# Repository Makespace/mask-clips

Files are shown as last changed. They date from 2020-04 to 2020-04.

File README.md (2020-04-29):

# Makespace Mask Clips

The documents covering the regulation, design and production of the Makespace Mask Clips

For the high-level overview of this activity, see https://web.makespace.org/covid-19/mask-clips/

* _Requirements_ – The device specification, regulations and risk assessments
* _Design Files_ – The mask clip design files
* _Materials_ – The materials and data sheets
* _Production_ – Manufacturing Standard Operating Procedure (SOP), Training and Worker/Batch Tracking
* _Documentation_ – The accompanying documentation and labelling for shipping

The _Manufacturing SOP_ document found in the _production_ directory is the key document describing the whole process, and the place to start if you want to learn about the activity.

The _Workstation Single Point Lessons_ ppt is also useful to get a feel for the activities that need to be performed.

The _requirements_ directory is good reading for context on how the essential safety requirements mandated in regulations are fulfilled by the design and documentation. This is what is required when the UK government relaxed the rules on PPE for hospitals from ‘at least CE marked’ to ‘meet essential safety requirements’.

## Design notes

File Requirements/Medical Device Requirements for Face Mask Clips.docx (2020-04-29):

Surgical Face Masks - For Clips Project

Surgical masks are Class 1 Medical Device.

“masks for the protection of the user (e.g. from the environment) are not medical devices, however, surgical masks (for use in an operating theatre) are medical devices as they are intended to protect the patient rather than the user”

Reference: https://assets.publishing.service.gov.uk/government/uploads/system/uploads/attachment_data/file/284505/Borderlines_with_medical_devices.pdf

Standard for surgical masks: Medical Face Masks - BS EN 14683:2019

“The main intended use of medical face masks is to protect the patient from infective agents and, additionally, in certain circumstances to protect the wearer against splashes of potentially contaminated liquids. Medical face masks may also be intended to be worn by patients and other persons to reduce the risk of spread of infections, particularly in epidemic or pandemic situations.”

“Type I medical face masks are used for patients in order to reduce the risk of the spread of infections, particularly in epidemic or pandemic situations. Type II masks are principally intended for use by healthcare professionals in an operating room or other medical settings with similar requirements.”

“The level of efficiency offered by a mask depends on a number of factors such as the filtration efficiency, quality of the material and the fit of the mask on the wearer’s face. Different designs are suited for different applications and the careful choice of mask is therefore important in order to achieve the desired result.”

“Due to the fact that used masks are considered highly contaminated, it is essential that:

— | the body of the mask is not touched by the fingers/hands of the wearer;”
— | a mask is worn covering the nose and mouth of the wearer, at no time a mask is hanging around the neck of the wearer”

- Use of the clip must not reduce Particle filtration, Bacterial Filtration, Breathability or blood fluid penetration

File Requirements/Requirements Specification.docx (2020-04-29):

# Requirements Specification

# 1. General Device Description & Intended Purpose

The product is a disposable cardboard attachment which sits on the back of the user’s head and is used to secure the elastic ear loops of disposable surgical masks.

It is intended to be used:

- To improve security of disposable Type IIR surgical masks with elastic ear loops against face compared to having no extra securement method
- To be more comfortable than the current recommended securement method (knots tied in the ear loops)

Type IIR surgical masks are a Class 1 medical device, and as such the face mask clip is an accessory to a medical device.

# 2. Specifications for Product

## 2.1. User Requirements

- The clip should deliver increased ear comfort compared to current best practice for surgical masks with ear loops (knotted ear loops)
- The clip should enable surgical masks with ear loops to be tightened such that they fit closely to the face
- Clip should be manufacturable at scale: projected best case 88635 surgical masks used in April (worst case: 354540)
- The clip is single use so disposable alongside face mask
- Clip must allow for different head sizes and be adjustable for tightness and comfort
- The edges and corners should not be sharp, such that they could rip gloves or cause injury
- Robust in expected usage conditions
- The clip must be suitable for a patient to wear whilst lying in bed
- There should be no increased risk of COVID infection due to use of the clip compared to current best practice
  2.2. Specification

User Requirement | Specification
The clip should deliver increased ear comfort compared to current best practice for surgical masks with ear loops (knotted ear loops) | Design must prevent the elastic ear loops being tightened against the user’s ears
The clip should enable surgical masks with ear loops to be tightened such that they fit closely to the face | The clip should enable surgical masks with ear loops to be tightened such that they fit closely to the face, such that the fit is as effective (or better) as with knotted ear loops
Clip should be manufacturable at scale: projected best case 88635 surgical masks used in April (worst case: 354540) | Design suitable for mass production of at least 10,000 units per day
The clip is single use so disposable alongside face mask | < 10p per item
| Suitable for incineration
| Minimum material per clip
Clip must allow for different head sizes and be adjustable for tightness and comfort | Design should enable users to adjust tightness
The edges and corners should not be sharp, such that they could rip gloves or cause injury | No sharp corners/edges
Robust in expected usage conditions | The clip must not break for a maximum usage duration of 4 hrs
The clip must be suitable for a patient to wear whilst lying in bed | Clip profile flat against head, no protrusions
There should be no increased risk of COVID infection due to use of the clip compared to current best practice | Must be provided clean (but not sterile, does NOT need to be sterilisable or resistant to cleaning products)
| Should not incur increased handling of ‘dirty’ PPE or hair/face/head when doffing
| The clip should not impact the usage or security of other PPE

Monitoring compliance with and the effectiveness of this document

This process forms part of a quality system accredited to International Standard EN ISO 9001:2015, EN ISO 13485:2016 and BS 70000:2017. The effectiveness of the process will be monitored in accordance with the methods given in the Quality Manual (CE-QS-QAM-4).

Equality and diversity statement

This document complies with the Cambridge University Hospitals NHS Foundation Trust service equality and diversity statement.

Disclaimer

It is your responsibility to check against the electronic library that this printed out copy is the most recent issue of this document.

Document management

Approval: | Sarah Greasley
MDAG approval:
Owning department: | Clinical Engineering Innovation
Author(s): | Sonya Sireau
Pharmacist: | n/a
File name: | Device Verification and Validation
Supersedes: | n/a
Version number: | 1.0 | Review date: | n/a
Local reference: | | Document ID:

Cambridge University Hospitals NHS Foundation Trust Requirements Specification

Clinical Engineering Innovation Medical Physics and Clinical Engineering

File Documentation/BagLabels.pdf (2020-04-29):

### Mask Clip

Design:
Lot No:
Name of Cutter:
Name of QC:
Date:
Material Batch No:
Number of Sheets:

### Mask Clip

Design:
Lot No:
Name of Cutter:
Name of QC:
Date:
Material Batch No:
Number of Sheets:

### Mask Clip

Design:
Lot No:
Name of Cutter:
Name of QC:
Date:
Material Batch No:
Number of Sheets:

### Mask Clip

Design:
Lot No:
Name of Cutter:
Name of QC:
Date:
Material Batch No:
Number of Sheets:

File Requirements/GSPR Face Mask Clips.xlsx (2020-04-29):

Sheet: Guidance
Template Q-pulse Reference: CE-ER-FRM-25 Revision 5
How to Complete the Checklist
Identity of the device | The manufacturer should identify the device, and where applicable the various configurations / variants covered by the checklist.
A. General Safety and Performance Requirements | Description of the Safety and Performance Requirements (SPR) as found in Annex I of the Medical Devices Regulation. The text is included non-edited. Also referred to as Essential Principle (EP)
B. Applicable to the device? | Is the listed Essential Principle applicable to the device? Here the answer is either ‘YES’ or ‘NO’. If the answer is ‘NO’ this should be explained briefly in the ‘method used to demonstrate conformity’ column. Example: For a device that does not incorporate biological substances, the answer to Essential Principle 5.8.2 would be ‘NO’ and, in the ‘method used to demonstrate conformity’ column, would include an explanation such as ‘The device does not incorporate biological substances.’
A / NA: | Identification whether the specific SPR is applicable (A) or not applicable (NA).
NOTE: It is required by the regulation to explain the reason why an essential requirement is not applicable. (e.g. for SPR 21 that the device is not connected to or equipped with a power source)
C. Method used to demonstrate conformity | In this column the manufacturer should state the type(s) of method(s) that they have chosen to use to demonstrate conformity e.g. the recognised standard(s), industry or in-house test method(s), comparison study(ies) or other method used.
D-F. Method reference | After having stated the method in the previous column, here the manufacturer should now name the title and reference of the recognised standard(s), industry or in-house test method(s), comparison study(ies) or other method used to demonstrate conformity. For standards, this should include the date of the standard and where appropriate, the clause(s) that demonstrates conformity with the relevant EP.
Horizontal Standards: | Specifies the relevant horizontal standards (horizontal standards are standards applicable to a broad range of medical devices, e.g. to electrically operated medical devices in general – e.g. EN 60601-1). Include the date of the standard and where appropriate, the clause(s) that demonstrates conformity with the relevant EP.
Vertical Standards: | Specifies the relevant vertical standards (vertical standards are standards applicable to a much more narrow range of products, e.g. to electrically operated infusions pumps – e.g. EN 60601-2-24). Include the date of the standard and where appropriate, the clause(s) that demonstrates conformity with the relevant EP.
Other Compliance Documentation: | Where a standard is not the appropriate means of ensuring compliance, identifies the method for alternative compliance documentation (e.g. in-house test method, etc.).
NOTE. When a requirement is dealt with in a horizontal as well as in a vertical standard, preference should be given to the more product specific standard, i.e. to the vertical standard
G. Reference to supporting controlled documents | This column should contain the reference to the actual technical documentation that demonstrates conformity to the essential principle, i.e. the certificates, test reports, validation reports, study reports or other documents that resulted from the method used to demonstrate conformity and its location within the STED.
Technical File Reference: | Reference to the Technical File information - Title and Q-pulse reference
NOTE: Machinery Directive | For medical devices which are also machinery within the meaning of Article 2 (a) of Directive 2006/42/EC on machinery:
 | Where relevant hazard exists, devices shall also meet the essential health and safety requirements of the Machinery Directive to the extent to which those essential health and safety requirements are MORE SPECIFIC than the essential requirements of the MDD (93/42/EEC)
Guidance from Global Harmonization Task Force GHTF/SG1/NO11:2008 (STED)
http://www.imdrf.org/docs/ghtf/archived/SG1/technical-docs/ghtf-sg1-n011-2008-principles-safety-performance-medical-devices-080221.pdf

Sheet: SPR Safety & Performance
Document Q-pulse reference:
Product identification (Identity of the Device): | Face Mask Clips
Author: | Sarah Greasley
Date: | 22/04/20
GENERAL SAFETY AND PERFORMANCE REQUIREMENTS CHECKLIST | Applicable to the device? | Method used to demonstrate conformity | Method reference |  |  | Reference to supporting controlled documents
GENERAL SAFETY AND PERFORMANCE REQUIREMENTS | A/NA | Method | Horizontal Standards | Vertical Standards | Other Compliance Documentation | Technical File Reference
1. Devices shall achieve the performance intended by their manufacturer and shall be designed and manufactured in such a way that, during normal conditions of use, they are suitable for their intended purpose. They shall be safe and effective and shall not compromise the clinical condition or the safety of patients, or the safety and health of users or, where applicable, other persons, provided that any risks which may be associated with their use constitute acceptable risks when weighed against the benefits to the patient and are compatible with a high level of protection of health and safety, taking into account the generally acknowledged state of the art. | A | Statement of Intended purpose Risk File
2. The requirement in this Annex to reduce risks as far as possible means the reduction of risks as far as possible without adversely affecting the benefit-risk ratio. | A | Risk File
3. Manufacturers shall establish, implement, document and maintain a risk management system. | A | Risk Management Process
Risk management shall be understood as a continuous iterative process throughout the entire lifecycle of a device, requiring regular systematic updating. In carrying out risk management manufacturers shall: | A | Risk Management Process
(a) establish and document a risk management plan for each device; | A | Risk Plan
(b) identify and analyse the known and foreseeable hazards associated with each device; | A | Risk File
(c) estimate and evaluate the risks associated with, and occurring during, the intended use and during reasonably foreseeable misuse; | A | Risk File
(d) eliminate or control the risks referred to in point (c) in accordance with the requirements of Section 4; | A | Risk File
(e) evaluate the impact of information from the production phase and, in particular, from the post-market surveillance system, on hazards and the frequency of occurrence thereof, on estimates of their associated risks, as well as on the overall risk, benefit-risk ratio and risk acceptability; and | A | Risk File PMS will also be conducted by speaking to the infection control team and asking for feedback from clinicians using the devices
(f) based on the evaluation of the impact of the information referred to in point (e), if necessary amend control measures in line with the requirements of Section 4. | A | Risk File
4. Risk control measures adopted by manufacturers for the design and manufacture of the devices shall conform to safety principles, taking account of the generally acknowledged state of the art. To reduce risks, Manufacturers shall manage risks so that the residual risk associated with each hazard as well as the overall residual risk is judged acceptable. In selecting the most appropriate solutions, manufacturers shall, in the following order of priority: | A | Risk File IFU / Training Manufacturing Documentation
(a) eliminate or reduce risks as far as possible through safe design and manufacture;
(b) where appropriate, take adequate protection measures, including alarms if necessary, in relation to risks that cannot be eliminated; and
(c) provide information for safety (warnings/precautions/contra-indications) and, where appropriate, training to users.
Manufacturers shall inform users of any residual risks. | A | IFU
5. In eliminating or reducing risks related to use error, the manufacturer shall: | N/A | N/A
(a) reduce as far as possible the risks related to the ergonomic features of the device and the environment in which the device is intended to be used (design for patient safety), and | A | The device will be shown to a clinican for feedback on the ergonomics of the design. This information will feed in to the risk file
(b) give consideration to the technical knowledge, experience, education, training and use environment, where applicable, and the medical and physical conditions of intended users (design for lay, professional, disabled or other users). | A | Feedback from the intended users will be obtained and incorpoorated into the design / IFU
6. The characteristics and performance of a device shall not be adversely affected to such a degree that the health or safety of the patient or the user and, where applicable, of other persons are compromised during the lifetime of the device, as indicated by the manufacturer, when the device is subjected to the stresses which can occur during normal conditions of use and has been properly maintained in accordance with the manufacturer's instructions. | A | The devices will be clearly labelled as single use. They will be designed and tested to be durable for this duration
7. Devices shall be designed, manufactured and packaged in such a way that their characteristics and performance during their intended use are not adversely affected during transport and storage, for example, through fluctuations of temperature and humidity, taking account of the instructions and information provided by the manufacturer. | A | Design and Manufacture Documentation No materials used will be affected by conditions likley to be experienced during distribution or storage
8. All known and foreseeable risks, and any undesirable side-effects, shall be minimised and be acceptable when weighed against the evaluated benefits to the patient and/or user arising from the achieved performance of the device during normal conditions of use. | A | Risk File
9. For the devices referred to in Annex XVI, the general safety requirements set out in Sections 1 and 8 shall be understood to mean that the device, when used under the conditions and for the purposes intended, does not present a risk at all or presents a risk that is no more than the maximum acceptable risk related to the product's use which is consistent with a high level of protection for the safety and health of persons. | A | Statement of Intended purpose Risk File
REQUIREMENTS REGARDING DESIGN AND MANUFACTURE
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

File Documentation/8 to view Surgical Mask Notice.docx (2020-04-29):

Disposable Surgical Mask Clips 002 DIRECTIONS FOR USE: This product is designed and intended only as a method of securing the elastic ear loops on surgical masks. This is a single use product. Dispose of product after use. One Size fits all. NON-STERILE. THIS PRODUCT IS NOT CE-MARKED. IT IS ONLY FOR USE DURING THE COVID-19 OUTBREAK Class I medical device Clinical Engineering, Box 152, Addenbrooke's Hospital, Cambridge, CB2 0QQ | Disposable Surgical Mask Clips 002 DIRECTIONS FOR USE: This product is designed and intended only as a method of securing the elastic ear loops on surgical masks. This is a single use product. Dispose of product after use. One Size fits all. NON-STERILE. THIS PRODUCT IS NOT CE-MARKED. IT IS ONLY FOR USE DURING THE COVID-19 OUTBREAK Class I medical device Clinical Engineering, Box 152, Addenbrooke's Hospital, Cambridge, CB2 0QQ
Disposable Surgical Mask Clips 002 DIRECTIONS FOR USE: This product is designed and intended only as a method of securing the elastic ear loops on surgical masks. This is a single use product. Dispose of product after use. One Size fits all. NON-STERILE. THIS PRODUCT IS NOT CE-MARKED. IT IS ONLY FOR USE DURING THE COVID-19 OUTBREAK Class I medical device Clinical Engineering, Box 152, Addenbrooke's Hospital, Cambridge, CB2 0QQ | Disposable Surgical Mask Clips 002 DIRECTIONS FOR USE: This product is designed and intended only as a method of securing the elastic ear loops on surgical masks. This is a single use product. Dispose of product after use. One Size fits all. NON-STERILE. THIS PRODUCT IS NOT CE-MARKED. IT IS ONLY FOR USE DURING THE COVID-19 OUTBREAK Class I medical device Clinical Engineering, Box 152, Addenbrooke's Hospital, Cambridge, CB2 0QQ
Disposable Surgical Mask Clips 002 DIRECTIONS FOR USE: This product is designed and intended only as a method of securing the elastic ear loops on surgical masks. This is a single use product. Dispose of product after use. One Size fits all. NON-STERILE. THIS PRODUCT IS NOT CE-MARKED. IT IS ONLY FOR USE DURING THE COVID-19 OUTBREAK Class I medical device Clinical Engineering, Box 152, Addenbrooke's Hospital, Cambridge, CB2 0QQ | Disposable Surgical Mask Clips 002 DIRECTIONS FOR USE: This product is designed and intended only as a method of securing the elastic ear loops on surgical masks. This is a single use product. Dispose of product after use. One Size fits all. NON-STERILE. THIS PRODUCT IS NOT CE-MARKED. IT IS ONLY FOR USE DURING THE COVID-19 OUTBREAK Class I medical device Clinical Engineering, Box 152, Addenbrooke's Hospital, Cambridge, CB2 0QQ
Disposable Surgical Mask Clips 002 DIRECTIONS FOR USE: This product is designed and intended only as a method of securing the elastic ear loops on surgical masks. This is a single use product. Dispose of product after use. One Size fits all. NON-STERILE. THIS PRODUCT IS NOT CE-MARKED. IT IS ONLY FOR USE DURING THE COVID-19 OUTBREAK Class I medical device Clinical Engineering, Box 152, Addenbrooke's Hospital, Cambridge, CB2 0QQ | Disposable Surgical Mask Clips 002 DIRECTIONS FOR USE: This product is designed and intended only as a method of securing the elastic ear loops on surgical masks. This is a single use product. Dispose of product after use. One Size fits all. NON-STERILE. THIS PRODUCT IS NOT CE-MARKED. IT IS ONLY FOR USE DURING THE COVID-19 OUTBREAK Class I medical device Clinical Engineering, Box 152, Addenbrooke's Hospital, Cambridge, CB2 0QQ | Basmati Rice 2015-01-22

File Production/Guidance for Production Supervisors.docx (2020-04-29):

# Makespace Surgical Mask Clip Production: Guidance for Production Supervisors

# Who Can Be a Production Supervisor?

The production supervisor should:

- Be familiar with every process involved in manufacturing, i.e. have been a volunteer on at least one previous shift
- Be a current Makespace member.
- Be trained on the laser-cutter, or have someone present who is.

# Planning

First-time supervisors should be supported by someone who has supervised a shift, or is familiar with most of the processes, e.g. Alaric or Jonathan. It may not be necessary for that person to be there for the whole time, but make sure you know who will be supporting you, and have contact numbers for arising issues.

Many people have worked extremely hard to set up production of the clips. You will be aware that part of the reason you are supervising a shift is so that they can have a rest. You should therefore be aware of common issues which are likely to arise, so you can handle them without contacting people outside the space. Equally, we have an obligation to manufacture to an acceptable standard, and if you’re not confident that can be achieved, it is better to call someone and get help than risk producing an unacceptable product.

## Issues that May Arise

The following things are the most likely, and you should know what to do or who to contact if they happen:

- Fire in the laser cutter, and or setting off the fire alarm
  - As per standard laser cutter practice, If the fire can be safely dealt with, blow it out (remember to remove mask), or use the fire extinguisher under the desk between the laser cutters. Otherwise raise the alarm with the break glass next to the exit door. The fire assembly point is in the main carpark out the front.
  - If the fire alarm goes off but the fire has been extinguished, call the estates department and let them know, so that the fire crew isn’t called out.
- Needing something from the office (e.g. packing tape, nitrile gloves). Will there be someone on shift with access (directors, some equipment owners)?
- Questions about the process, e.g. what quality issues are acceptable. You should be familiar with most of the things that can go wrong, e.g.smoke stains, burn marks Familiarise yourself with the operating procedures (SOP). (https://drive.google.com/open?id=1OLOXmGqOo-xyjaSSg0BIGB7wWn_eqW5IFoa0JmBFgyE) Try to answer most questions yourself, remember if it’s only one or two clips affected, it’s safer to reject them. Don’t worry about the occasional false-reject.
- Errors with data entry. Volunteers will sometimes make errors, e.g. forgetting to retire jobs, selecting the wrong job etc. If Dan is there, he can correct those. If you are confident to do so, you can correct them yourself in the production spreadsheet (https://drive.google.com/open?id=1U6qBrt-kxL_5vciE0YUX_pbPlAORHrKN3EtSc_qxcnQ).
- Process Changes. Volunteers may suggest process changes and improvements. If they can be included within the existing SOPs, they may be acceptable. If not, they should be rejected or approved by Mark Mellors.

# Running the Shift

1. Try to speak with the production supervisor for the previous shift before that shift ends, so you understand any issues such as shortages before your shift starts.
2. Arrive about 30-60 minutes before the shift starts to give time for reviewing the state of the workplace, cleaning, and any corrective actions needed. If you’re running an afternoon shift after a morning shift has run, you should be able to speak with the previous supervisor then.
3. When the volunteers arrive, brief them on:
  a. Building issues: Fire safety - fire extinguisher location, break glass, locations of exits; Toilets; Breakroom. Clean area and dirty area.
  b. Check if they are symptomatic or have been exposed. Send home if exposed in the last 14 days.
  c. Procedure for cleaning and doffing PPE. check no-one is wearing a valved mask - replace with a cotton one or cover the valve
  d. How to use the IT system, and why (medical manufacturing, traceability).
4. Anyone who arrives early can start on any outstanding cleaning.
5. Assign people to workstations, and ensure they are trained, either by another volunteer, or yourself. After a few minutes, check on them to make sure they’re happy with what they’re doing, and following procedures. Periodically check in with people, and check that they’re retiring cards correctly.
6. Try to keep work flowing consistently through the process. There should be roughly equal numbers of batches queued at each station. If one process is getting ahead or behind, move volunteers around to balance it out. This will help to minimise work in progress (WIP).
7. Encourage volunteers to work in full batches, and not stop mid-batch. Organising a tea-break in the middle of the shift is usually welcome!
8. Keep an eye on stock levels, both of WIP and input materials, to avoid bottlenecks.
9. At the end of the shift, all workstations should be tidied ready for the next shift. Ensure that there are no partially-completed batches. Warn volunteers before the end of the shift, so that they don’t start batches without time to complete them.
10. Ensure all the volunteers sign out when they leave.

# Production Database Cheat Sheet

The Chrome-books which are set up at each station for production tracking feed into this database: production spreadshee (https://drive.google.com/open?id=1L1GX-7yRM-hOOdorrYTUK3-CFr-ufjhGhRJ_fhcEF2Y)t, on the ‘JobLog’ tab. Further details about the spreadsheet will be documented in the README (https://github.com/axiomsofchoice/jobcardsystem) of the published source code

Key operations you should be aware of:

1. Comments can always be added in the comments column, separated by a ‘;’. E.g. if there is already a comment, add a ‘;’, then your comments.
2. If you make a change, add a comment, e.g. Fixed consumed job, used 101, not 100.
3. Sometimes volunteers put in the wrong ‘consumed lots’ information. If you know what they did, you can correct the lots consumed by changing the numbers in this column.
4. Periodically check the contents of each of the tabs in the spreadsheet in case there is an issue that needs to be brought to someone’s attention (e.g. someone ticks yes for has symptoms) or there is a data entry issue that needs correcting. Important: values in the comments column are not automatically used for traceability, they are only for humans, so ensure the values in the “Lots Consumed” column accurately reflect what occurred.
5. The values recorded in “Worker”, “Additional Worker 1”, “Additional Worker 2” and “Retired by” must correspond precisely to the values given in the “Workers” sheet, including case and spelling.
6. Often, volunteers forget to retire jobs after they have been consumed. You can retire a job by going to the home page and selecting “Retire Job Card”.
7. If a volunteer forgets to mark a job as complete there is currently no way to correct this in the UI and it must be corrected via the spreadsheet.
8. If a volunteer accidentally retires a job, you can ‘unretire’ it by clearing the “Lot Consumed Time” and “Retired by” entries for that job.
9. Duplicate jobs sometimes occur although now less frequently. If this happens, identify the job that should not be there and change the workstation to “Void”, appending a note in the comment field.
10. At the end of a shift, a backup should be made of the spreadsheet, which can be done by going to File > Download.
11. Any bugs can be raised on the Github issue tracker (https://github.com/axiomsofchoice/jobcardsystem/issues).

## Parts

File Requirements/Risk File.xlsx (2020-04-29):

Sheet: Title
Medical Physics and Clinical Engineering |  |  |  | Addenbrookes Hospital
Clinical Engineering / R&D
Risk File |  |  |  | CE-ER-FRM-22
 |  | Product Identification | Surgical Mask Clips
 |  | Document Q-Pulse reference
 |  | Doc. Name | Risk File - Mask Clips
 |  | Mandatory Supporting Documents | Q-Pulse reference
 |  | Risk Management Process
 |  | Risk Plan
 |  | Risk Report
 | Product description and intended use
 | The product is a disposable attachment which is used to secure the elastic ear loops of disposable surgical masks by providing an attachment point on the back of the head. It is intended to be used: To improve security of disposable Type IIR surgical masks with elastic ear loops against face compared to having no extra securement method To be more comfortable than the current recommended securement method (knots tied in the ear loops) Type IIR surgical masks are a Class 1 medical device, and as such the face mask clip is an accessory to a medical device.
Cambridge University Hospitals NHS Foundation Trust |  |  |  |  | Page 1 of 4
This document complies with the Cambridge University Hospitals NHS Foundation Trust service Equality and Diversity statement and must be read in conjunction with Addenbrookes Hospital Policies & Procedures. It is your responsibility to check against the electronic library that this printed out copy is the most recent issue of this document. All changes required should be submitted via Q-Pulse Document module (Change request).
Filename: 008_Risk Evaluation Table
Document No.: CE-ER-FRM-15 |  |  | Version No.: 5 | Active on Q-Pulse & Published

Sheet: Revision Table
Document History
Date | Identification | Description | Name
2020-08-04 | 1.0 | Created (Draft) | Sonya Sireau

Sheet: Risk Evaluation Criteria
CUH Risk management strategy and policy 2019-2019
 | CUH Risk management strategy and policy 2019-2020
Source | CUH Risk management strategy and policy 2019-2020, http://merlin/Lists/DMSRecords/DispRecordTabsDoc.aspx?ID=18427
Adaptations | The risk scoring matrix and grading system has been adapted to enable the CEI team to better track and manage risks that are yet to be determined, or cannot be determined.
Notes | Risk evaluation is for injury or damage to the health of people, or damage to property or the environment, and does include risks surrounding data security. It should NOT consider project or financial impacts. These should instead be considered in the Project Viability Assessment.
 | Risk Evaluation
 | Severity Score |  | Likelihood Score |  |  |  |  |  |  | Grading Risk
 |  |  | 1 | 2 | 3 | 4 | 5 | TBD | CBD | 1-3 | Low risk | No action required
 |  |  | Rare | Unlikely | Possible | Likely | Almost Certain | To be determined | Cannot be determined | 4-6 | Moderate risk | Risk reduction if practicable
 | 1 | Negligible | 1 | 2 | 3 | 4 | 5 | 25 | 25 | 8-12 | High risk | Risk reduction if practicable, cost benefit analysis required for risks that cannot be practibably lowered
 | 2 | Minor | 2 | 4 | 6 | 8 | 10 | 25 | 25 | 15-25 | Significant risk | Unnacceptable risk
 | 3 | Moderate | 3 | 6 | 9 | 12 | 15 | 25 | 25 | TBD | To be determined | Activities required to define risk likelihood or severity
 | 4 | Major | 4 | 8 | 12 | 16 | 20 | 25 | 25 | CBD | Can't be determined | Treat as unnacceptable and define control measures, or justify lower risk score
 | 5 | Catastrophic | 5 | 10 | 15 | 20 | 25 | 25 | 25
 | TBD | To be determined | 25 | 25 | 25 | 25 | 25 | 25 | 25
 | CBD | Cannot be determined | 25 | 25 | 25 | 25 | 25 | 25 | 25
 | Likelihood Score
 |  | 1 | 2 | 3 | 4 | 5
 | Descriptor | Rare | Unlikely | Possible | Likely | Almost Certain
 | Frequency | This will probably never happen/recur | Do not expect it to happen/recur but it is possible | Might happen or recur occasionally | Will probably happen/recur but it is not a persisting issue | Will undoubtedly happen/recur,possibly frequently
 | Severity Score
 |  | 1 | 2 | 3 | 4 | 5
 | Descriptor | Negligible | Minor | Moderate | Major | Catastrophic
 | Impact on the safety of patients, staff or public (physical/psychological harm) | Minimal injury requiring no/minimal intervention or treatment. | Minor injury or illness, requiring minor intervention. Increase in length of hospital stay by 1-3 days Requiring time off work for >3 days | Moderate injury requiring professional intervention. Requiring time off work for 4-14 days Increase in length of hospital stay by 4-15 days RIDDOR/agency reportable incident An event which impacts on a small number of patients. | Major injury leading to long-term incapacity/disability. Increase in length of hospital stay by >15 days. Mismanagement of patient care with longterm effects. Requiring time off work for >14 days | Incident leading to death. Multiple permanent injuries or irreversible health effects. An event which impacts on a large number of patients.
 | Quality of treatment | Peripheral element of treatment or service suboptimal Informal complaint/inquiry | Overall treatment or service suboptimal Single failure to meet internal standards | Treatment or service has significantly reduced in effectiveness Repeated failure to meet internal standards | Non-compliance with national standards with significant risk to patients if unresolved Multiple complaints/ independent review Low performance rating Critical report | Totally unacceptable level or quality of treatment/service Gross failure of patient safety if findings not acted on Inquest/ombudsman inquiry Gross failure to meet national standards
 | Personal information | No risk to confidential staff or patient data | Occassional/one-off cases of personal data exposure within CUH | Data exposure within CUH | Public exposure of personal data Exposure of personal data to entities who may use that data against the best interest of the person to whom the data belongs | Large scale public exposure of personal data Exposure of personal data to entities who will use that data against the best interest of the person to whom the data belongs
 | Envrionmental impact | Minimal or no impact on the environment | Minor impact on environment | Moderate impact on environment | Major impact on environment | Catastrophic impact on environment
 | Environmental impact | Minimal or no impact on the environment | Minor impact on environment | Moderate impact on environment | Major impact on environment | Catastrophic impact on environment

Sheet: Benefit Evaluation Criteria
008_Risk Evaluation Table
 | Benefit Evaluation Criteria
Source | Developed by CEI
Adaptations | n/a
Notes | Benefit evaluation is for assessing impact on positive impact on clinical outcome, the patient’s quality of life, outcomes related to diagnosis, positive impact from diagnostic devices on clinical outcomes, or positive impact on public health or patient management. It should NOT consider project or financial impacts. These should instead be considered in the Project Viability Assessment.
 | Risk Evaluation
 | Benefit Size Score |  | Certainty Score |  |  |  |  | Grading Risk
 |  |  | 1 | 2 | 3 | 4 | 5 | 15-25 | Large, clear benefit
 |  |  | Very unlikely to be realised | Unlikely | Possible | Likely | Almost Certain | 2020-10-12 | Reasonable benefit
 | 1 | Negligible | 1 | 2 | 3 | 4 | 5 | 2020-05-09 | Small benefit
 | 2 | Minor | 2 | 4 | 6 | 8 | 10 | 2020-01-04 | Very little benefit
 | 3 | Moderate | 3 | 6 | 9 | 12 | 15
 | 4 | High | 4 | 8 | 12 | 16 | 20
 | 5 | Very High | 5 | 10 | 15 | 20 | 25
 | Likelihood Score
 |  | 1 | 2 | 3 | 4 | 5
 | Descriptor | Rare | Unlikely | Possible | Likely | Almost Certain
 | Frequency | Possible but quite unlikely outcome of the project/extremely uncertain outcome of the project | Possible outcome of the project, but uncertain | Possible outcome of the project | A likely outcome of the project | Will undoubtedly happen as an outcome of the project if completed successfully
 | Impact Score
 |  | 1 | 2 | 3 | 4 | 5
 | Descriptor | Negligible | Minor | Moderate | High | Very High
 | Medical Benefit | No measurable impact on medical outcomes No measurable impact on patient experience Minor anecdotal benefit | Minor measurable impact on medical outcomes Minor measurable impact on patient experience Moderate anecdotal benefit | Moderate measurable impact on medical outcomes Moderate measurable impact on patient experience Large anecdotal benefit (e.g. patients happy to engage with a home treatment method where they otherwise wouldn't) | Significant measurable impact on key medical outcomes Significant measurable impact on patient experience | Measurable life-saving impact
 | Scale of impact | Hospital, short term or one-off Less than 100 patients per year | Hospital Hundreds of patients per year | Hospital or regional Thousands of patients per year | National 10s of thousands of patients per year | International 100s of thousands of patients affected per year
 | Clinical benefit | No measurable impact | Minor increase in number of patients treated for a given resource (e.g. reduced hospital stay Minor decrease in resource required to treat a given number of patients (lower cost per intervention, reduction in consultant time per appointment) Minor improvement in service quality (e.g. speed of diagnosis, error reduction) | Moderate increase in number of patients treated for a given resource (e.g. reduced hospital stay Moderate decrease in resource required to treat a given number of patients (lower cost per intervention, reduction in consultant time per appointment) Moderate improvement in service quality (e.g. speed of diagnosis, error reduction) | Large increase in number of patients treated for a given resource (e.g. reduced hospital stay Large decrease in resource required to treat a given number of patients (lower cost per intervention, reduction in consultant time per appointment) Large improvement in service quality (e.g. speed of diagnosis, error reduction) | Transformative increase in number of patients treated for a given resource (e.g. reduced hospital stay Transformative decrease in resource required to treat a given number of patients (lower cost per intervention, reduction in consultant time per appointment) Transformative improvement in service quality (e.g. speed of diagnosis, error reduction)

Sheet: Overall Benefit Risk
008_Risk Evaluation Table
Benefit Risk Summary
 | Surgical Mask Clip
 | Overall Benefit: | 18
 | Residual Risk: | 5
 | Summary of benefit: | Surgical masks with ear loops need to be secured more firmly to the face than ear loops allow - greater security of the mask has a moderate to significant impact on the risk of transmission. This solution enables this security to take place without causing additional discomfort to the wearer compared to wearing an un-secure mask.
 | Summary of risk: | There are two areas of risk which may increase the risk of COVID-19 transmission to staff compared with continuing to use knots. First is the residual risk that COVID-19 may be transmitted from manufacturer to user via the clip surface. Second is the residual risk associated with increased handling of hair during doffing if the clip becomes tangled.
 | Actions summary: | Continue to evaluate designs whilst in use.
Optional: Benefit-risk summary for current state-of-the-art
 | Knotted ear loops
 | Overall Benefit: | 16
 | Residual Risk: | 20
 | Summary of benefit: | Surgical masks with ear loops need to be secured more firmly to the face than ear loops allow - greater security of the mask has a moderate impact on the risk of transmission. This solution enables the mask to be secured to the face much better than not having knots in the ear loops.
 | Summary of risk: | Discomfort from the tightened ear loops is causing pain/injury amongst a large proportion of staff. For some staff, this is increasing level of strees and affecting ability to provide care. For a minority of staff, there is a refusal to accept these masks and staff are insisting on FFP3 masks instead. This could cause future shortages through unnecescary use of PPE. It is also likely that some staff will bring in thei own alternatives which carry additional risk
 | Actions summary:
 | NOT APPLICABLE - product proposal is due to absence of availability of state-of-the-art

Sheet: Device Benefit Evaluation
008_Risk Evaluation Table
Benefit Evaluation Table for medical and clinical benefits associated with the medical device
Source | Developed by CEI
 | Overall Benefit: | 18 | Evaluate overall residual medical/clinical benefit. This can be estimated as the largest single RPN score.
S = severity, L = likelihood, RPN = Risk Priority Number
Unique ID for hazard plus control measure - useful for referencing hazards in other documents | Brief note explaining benefit | Brief note explaining consequence of benefit | Define any investigatory activities/follow up actions when it is too early to define impact/likelihood | Impact | Likelihood | Score
ID | Benefit | Consequence | Investigatory activities required | S | L | RPN
FV01 | Surgical masks are held more securely to face, increasing efficacy and decreasing risk of transmission of virus from staff to patient/patinet to staff. | Moderate reduction of staff risk in contracting COVID-19 |  | 4 | 4 | 16
FV02 | Masks are secured more comfortably than alternative methods. | Greater adherence to protocol, reduction in risk of staff contracting covid. |  | 4 | 3 | 12
FV03 | Masks are secured more comfortably than alternative methods. | Increased comfort |  | 2 | 5 | 10
FV04 | Masks are secured more comfortably than alternative methods. | Staff will not insist on wearing FFP3 masks to prevent ear pain, so less PPE will be wasted. This may prevent future infections casued by lack of PPE, or inadequate care due to lack of PPE. |  | 4 | 3 | 12
 |  |  |  |  |  | 0
 |  |  |  |  |  | 0
 |  |  |  |  |  | 0
Benefit Evaluation Table for medical and clinical benefits associated with best alternative (knots in ear loops)
Source | Developed by CEI
 | Overall Benefit: | 16 | Evaluate overall residual medical/clinical benefit. This can be estimated as the largest single RPN score.
S = severity, L = likelihood, RPN = Risk Priority Number
Unique ID for hazard plus control measure - useful for referencing hazards in other documents | Brief note explaining benefit | Brief note explaining consequence of benefit | Define any investigatory activities/follow up actions when it is too early to define impact/likelihood | Impact | Likelihood | Score
ID | Benefit | Consequence | Investigatory activities required | S | L | RPN
FV01 | Surgical masks are held more securely to face, increasing efficacy and decreasing risk of transmission of virus from staff to patient/patinet to staff. | Moderate reduction of staff risk in contracting COVID-19 |  | 4 | 4 | 16
 |  |  |  |  |  | 0
 |  |  |  |  |  | 0
 |  |  |  |  |  | 0
 |  |  |  |  |  | 0
 |  |  |  |  |  | 0
 |  |  |  |  |  | 0
 |  |  |  |  |  | 0
 |  |  |  |  |  | 0
 |  |  |  |  |  | 0
 |  |  |  |  |  | 0
 |  |  |  |  |  | 0
 |  |  |  |  |  | 0
 |  |  |  |  |  | 0
 |  |  |  |  |  | 0
 |  |  |  |  |  | 0
 |  |  |  |  |  | 0
 |  |  |  |  |  | 0
 |  |  |  |  |  | 0
 |  |  |  |  |  | 0
 |  |  |  |  |  | 0
 |  |  |  |  |  | 0
 |  |  |  |  |  | 0
 |  |  |  |  |  | 0
 |  |  |  |  |  | 0
 |  |  |  |  |  | 0
 |  |  |  |  |  | 0
 |  |  |  |  |  | 0
 |  |  |  |  |  | 0
 |  |  |  |  |  | 0
 |  |  |  |  |  | 0
 |  |  |  |  |  | 0
 |  |  |  |  |  | 0
 |  |  |  |  |  | 0
 |  |  |  |  |  | 0
 |  |  |  |  |  | 0
 |  |  |  |  |  | 0
 |  |  |  |  |  | 0
 |  |  |  |  |  | 0
 |  |  |  |  |  | 0
 |  |  |  |  |  | 0
 |  |  |  |  |  | 0
 |  |  |  |  |  | 0
 |  |  |  |  |  | 0

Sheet: Device Risk Evaluation - clips
Risk Evaluation Table for health hazards associated with the medical device that may impact users or patients
Scope: | injury or damage to the health of people, or damage to property or the environment
Source | Developed by CEI
 | Device: | Surgical Face Mask Clips
 | Residual Risk: | 5 | Evaluate overall residual medical/clinical risk following the process described in the Risk Management Process CE-ER-PRO-14
 | Explanation:
S = severity, L=likelihood
Unique ID for hazard plus control measure | Brief note describing hazard | Brief note expalining impact/consequences of hazard | Severity | Likelihood | Score | Define any investigatory activities/follow up actions when it is too early to define a risk control activity | Define activities to control risk (or summarise existing evidence) | Provide a Q-Pulse reference, or location reference to the Technical File | Provide a date of completion for risk control activitie, to confim the activity has been completed | Severity | Likelihood | Score | Detail outcome - is the risk acceptable? If not, is a further risk control measure required (please enter the same hazard with a different ID and repeat the risk evaluation and control prcoess)? Alternatively, is a risk benefit analysis required? | Optional - tick if a risk/benefit is required | Please summarise the outcome of the risk/benefit analysis | If not in this document, please supply a Q-Pulse reference or location reference to the Technicla Filefor location of risk-benefit analysis
ID | Hazard | Consequence | S | L | RPN | Further activities required | Risk Control Measures | Supporting Documentation | Date carried out dd/mm/yyyy | S2 | L2 | RPN2 | Outcome | Risk/Benefit required? | Risk Benefit Outcome | Supporting Documentation2
FV01 | Interference with donning of PPE - Excessive touching of hair, or increased likelihood of contacting inside of mask compared to no clip. | Increase likelihood of clinician contacting COVID. Note, they should be donning PPE with cleaned, non-gloved hands. | 5 | 1 | 5 |  | Design & user testing | Verification & Validation | 20/04/2020 | 5 | 1 | 5 | Unacceptable | Yes | Risk acceptable
FV02 | Interference with doffing of PPE - increased contact time with hair, increased likelihood of contacting outside surface of mask. Note, PPE will be doffed using clean, non-gloved hands. | Increase likelihood of clinician contracting COVID. | 5 | 2 | 10 |  | Design & user testing. Instructions for use showing pictures of donning and doffing | Verification & Validation | 20/04/2020 | 5 | 1 | 5 | Unacceptable | Yes | Risk acceptable
FV03 | Interference with doffing of PPE - clip falls off onto floor before being placed in bin. Note, PPE will be doffed using clean, non-gloved hands. | Increase likelihood of clinician contacting COVID, since clinician will have to handle unclean clip to transfer to bin. | 5 | 2 | 10 | Is there a protocol in place for e.g. surgical masks that miss the bin | Design & user testing | Verification & Validation | 20/04/2020 | 5 | 1 | 5 | Unacceptable | Yes | Risk acceptable
FV04 | User hair snagging | Hands are clean, but hair may provide a transmission surface to clean hands. Worst case - contract COVID, death. | 5 | 2 | 10 |  | Design selection & user testing | Verification & Validation | 20/04/2020 | 5 | 1 | 5 | Unacceptable | Yes | Risk acceptable
FV05 | Catches with cap | Increased handling of dirty PPE when doffing. | 5 | 2 | 10 |  | Design & user testing | Verification & Validation | 20/04/2020 | 5 | 1 | 5 | Unacceptable | Yes | Risk acceptable
FV06 | Interfers with visor / cap | Decreases effectiveness of other PPE. | 5 | 1 | 5 |  | Design & user testing | Verification & Validation | 20/04/2020 | 5 | 1 | 5 | Unacceptable | Yes | Risk acceptable
FV07 | Clip breaks | Foreign object in clinical environment | 3 | 3 | 9 | Is there an existing protocol for this? | Material properties Geometry designed to avoid stress concentration Designed to handle sweat QC to avoid manufacturing defects that may lead to breakage | Verification & Validation | 20/04/2020 | 3 | 1 | 3 | Acceptable | Yes | Risk acceptable
FV08 | Viral transmission from manufacturer to user via persistence of virus on device materials | Infection of clinical staff member, who may infect other staff or patients - worst possible consequence is death | 5 | 3 | 15 | Check longevity of viable virus in literature | Process control to ensure risk of transmission from manufacturer to product is minimised | Manufacturing SOP | 22/04/2020 | 5 | 1 | 5 | Unacceptable | Yes | Risk acceptable
FV09 | Viral transmission due to presence of virus on material for visor before arrival at the manufacturing facility. Transmission to manufacturing staff, or to clinical staff. | Infection of clinical staff member, who may infect other staff or patients - worst possible consequence is death | 5 | 3 | 15 | Risk assess different material supply options | Prevention through material handling controls | Manufacturing SOP | 22/04/2020 | 5 | 1 | 5 | Unacceptable | Yes | Risk acceptable
FV10 | Material of mask clip irritates skin | Skin damage | 2 | 3 | 6 |  | Ensure material selected is appropriate for skin contact up to 4 hr | Waiting on data sheets - however, low risk that food grade cardboard and food grade polypropylene will cause harm | 22/04/2020 | 2 | 2 | 4 | Acceptable | Yes | Risk acceptable
FV11 | Mask does not fit face as well as without the clip | Increase likelihood of clinician contracting COVID. | 5 | 2 | 10 | Initial evaluation by range of staff required - could we put a QR code on visor to a GoogleForm? | Testing with a range of different head size users . Clips are designed so that masks fit better | Verification & Validation | 20/04/2020 | 5 | 1 | 5 | Unacceptable | Yes | Risk acceptable
FV12 | Clip intereferes with hairstyle (e.g. ponytail) and fit is poor on face | Increase likelihood of clinician contracting COVID. | 5 | 3 | 15 | Initial evaluation by range of staff required - could we put a QR code on visor to a GoogleForm? | Testing with a range of different hairstyles. Clips can be worn in a variety of ways to accomodate different hairstyles | Verification & Validation | 20/04/2020 | 5 | 1 | 5 | Unacceptable | Yes | Risk acceptable
FV13 | Sharp edges cause cut when being handled | Delay in clincian seeing patient whilst cut is cleaned and covered. | 3 | 2 | 6 |  | Quality control during manufacturing process Design | Verification & Validation | 20/04/2020 | 3 | 1 | 3 | Acceptable
FV14 | Clinician handles mutiple clips when picking own clip up | Clinican to clinician transmission of COVID via clips wiating to be used. Worst scenario: death. | 5 | 2 | 10 | Discussion with infection control | Standard practice is that clinicians will all have clean ahnds when donning ppe | Device prescrition (sign off of design for container from Infection Control) | 22/04/2020 | 5 | 1 | 5 | Unacceptable | Yes | Risk acceptable
 |  |  |  |  | 0 |  |  |  |  |  |  | 0
 |  |  |  |  | 0 |  |  |  |  |  |  | 0
 |  |  |  |  | 0 |  |  |  |  |  |  | 0
 |  |  |  |  | 0 |  |  |  |  |  |  | 0
 |  |  |  |  | 0 |  |  |  |  |  |  | 0
 |  |  |  |  | 0 |  |  |  |  |  |  | 0
 |  |  |  |  | 0 |  |  |  |  |  |  | 0
 |  |  |  |  | 0 |  |  |  |  |  |  | 0
 |  |  |  |  | 0 |  |  |  |  |  |  | 0
 |  |  |  |  | 0 |  |  |  |  |  |  | 0
 |  |  |  |  | 0 |  |  |  |  |  |  | 0
 |  |  |  |  | 0 |  |  |  |  |  |  | 0
 |  |  |  |  | 0 |  |  |  |  |  |  | 0
 |  |  |  |  | 0 |  |  |  |  |  |  | 0
 |  |  |  |  | 0 |  |  |  |  |  |  | 0
 |  |  |  |  | 0 |  |  |  |  |  |  | 0
 |  |  |  |  | 0 |  |  |  |  |  |  | 0
 |  |  |  |  | 0 |  |  |  |  |  |  | 0
 |  |  |  |  | 0 |  |  |  |  |  |  | 0
 |  |  |  |  | 0 |  |  |  |  |  |  | 0
 |  |  |  |  | 0 |  |  |  |  |  |  | 0
 |  |  |  |  | 0 |  |  |  |  |  |  | 0
 |  |  |  |  | 0 |  |  |  |  |  |  | 0
 |  |  |  |  | 0 |  |  |  |  |  |  | 0
 |  |  |  |  | 0 |  |  |  |  |  |  | 0
 |  |  |  |  | 0 |  |  |  |  |  |  | 0
 |  |  |  |  | 0 |  |  |  |  |  |  | 0
 |  |  |  |  | 0 |  |  |  |  |  |  | 0
 |  |  |  |  | 0 |  |  |  |  |  |  | 0
 |  |  |  |  | 0 |  |  |  |  |  |  | 0
 |  |  |  |  | 0 |  |  |  |  |  |  | 0
 |  |  |  |  | 0 |  |  |  |  |  |  | 0
 |  |  |  |  | 0 |  |  |  |  |  |  | 0
 |  |  |  |  | 0 |  |  |  |  |  |  | 0
 |  |  |  |  | 0 |  |  |  |  |  |  | 0
 |  |  |  |  | 0 |  |  |  |  |  |  | 0
 |  |  |  |  | 0 |  |  |  |  |  |  | 0
 |  |  |  |  | 0 |  |  |  |  |  |  | 0
 |  |  |  |  | 0 |  |  |  |  |  |  | 0
 |  |  |  |  | 0 |  |  |  |  |  |  | 0
 |  |  |  |  | 0 |  |  |  |  |  |  | 0
 |  |  |  |  | 0 |  |  |  |  |  |  | 0
 |  |  |  |  | 0 |  |  |  |  |  |  | 0
 |  |  |  |  | 0 |  |  |  |  |  |  | 0
 |  |  |  |  | 0 |  |  |  |  |  |  | 0
 |  |  |  |  | 0 |  |  |  |  |  |  | 0
 |  |  |  |  | 0 |  |  |  |  |  |  | 0
 |  |  |  |  | 0 |  |  |  |  |  |  | 0
 |  |  |  |  | 0 |  |  |  |  |  |  | 0
 |  |  |  |  | 0 |  |  |  |  |  |  | 0
 |  |  |  |  | 0 |  |  |  |  |  |  | 0
 |  |  |  |  | 0 |  |  |  |  |  |  | 0
 |  |  |  |  | 0 |  |  |  |  |  |  | 0
 |  |  |  |  | 0 |  |  |  |  |  |  | 0
 |  |  |  |  | 0 |  |  |  |  |  |  | 0
 |  |  |  |  | 0 |  |  |  |  |  |  | 0
 |  |  |  |  | 0 |  |  |  |  |  |  | 0
 |  |  |  |  | 0 |  |  |  |  |  |  | 0
 |  |  |  |  | 0 |  |  |  |  |  |  | 0
 |  |  |  |  | 0 |  |  |  |  |  |  | 0
 |  |  |  |  | 0 |  |  |  |  |  |  | 0
 |  |  |  |  | 0 |  |  |  |  |  |  | 0
 |  |  |  |  | 0 |  |  |  |  |  |  | 0
 |  |  |  |  | 0 |  |  |  |  |  |  | 0
 |  |  |  |  | 0 |  |  |  |  |  |  | 0
 |  |  |  |  | 0 |  |  |  |  |  |  | 0
 |  |  |  |  | 0 |  |  |  |  |  |  | 0
 |  |  |  |  | 0 |  |  |  |  |  |  | 0
 |  |  |  |  | 0 |  |  |  |  |  |  | 0
 |  |  |  |  | 0 |  |  |  |  |  |  | 0
 |  |  |  |  | 0 |  |  |  |  |  |  | 0
 |  |  |  |  | 0 |  |  |  |  |  |  | 0
 |  |  |  |  | 0 |  |  |  |  |  |  | 0
 |  |  |  |  | 0 |  |  |  |  |  |  | 0
 |  |  |  |  | 0 |  |  |  |  |  |  | 0
 |  |  |  |  | 0 |  |  |  |  |  |  | 0
 |  |  |  |  | 0 |  |  |  |  |  |  | 0
 |  |  |  |  | 0 |  |  |  |  |  |  | 0
 |  |  |  |  | 0 |  |  |  |  |  |  | 0
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

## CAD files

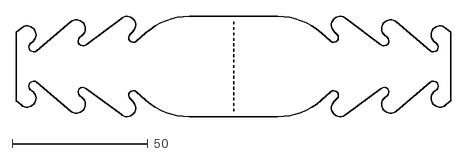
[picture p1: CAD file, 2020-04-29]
Design Files/46430-MS Addenbrooks Firstan Clip.dxf
160.0 x 37.0

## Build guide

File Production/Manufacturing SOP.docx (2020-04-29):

# Manufacturing SOP: Surgical Mask Clip

Author: Mark Mellors Version 1 18 April 2020

# Purpose

To define:

- Process for cutting clips
- Precautions to prevent spread of COVID-19 by contamination of clips during manufacture and distribution
- Means of recording implementation of processes and precautions.

# Scope

Qualified staff/volunteers manufacturing the Addenbrooke’s approved design(s) of Surgical Mask Clips at MakeSpace, Mill Lane, Cambridge.

# Responsibilities

All:

- To ensure MakeSpace facility remains a “safe zone”, free of virus as far as possible
- Not to enter the MakeSpace facility if you show any symptoms that could indicate COVID-19, or you have been in recent contact with anyone showing symptoms.
- Report any symptoms that arise within 5 days of working in the MakeSpace facility to cei@addenbrookes.nhs.uk

Supervisor:

- Ensure process is conducted according to SOP
- Document & report any non-conformances

Technician:

- Conduct cleaning, cutting and packaging as described
- Wear PPE as required.

# Hygiene Precautions

## a. Entry to workspace & Designation of Areas

Preventing the virus entering the workspace area is a high priority.

- All personnel will first enter “Contamination not controlled”
- On entry to this area, all personnel must remove outdoor clothing and store it in “Staff outer vestibule area”, NOT on the worktables
- All personnel must record time of entry and exit and sign a statement of general good health, stating duration of isolation and any potential opportunities for virus transmission - this will allow traceability in case of subsequent symptoms appearing
- Before entering the “Production Area”:
  - Use the “Prep Area” to wash hands thoroughly
  - Don PPE
- To transition back from the “Production Area” to “Dirty Goods In”
  - Use the “Prep Area” to doff PPE
- To enter or leave the “Contamination controlled”, you must observe the strict prohibition of the gangway.
- To protect operators, workstations are single operator only
- WIP parts must only be placed on the work surfaces labelled on the diagram
- The operator work stations mapped out (per the standardised work sheet below) have been positioned to allow a minimum of 2m clearance between operators to minimise operator cross-contamination risks.

TO OUTSIDE

CORRIDOR

KEY

Door

Work Table

Laser Cutter

Laser Cutter Computer

Other Equipment

Sink

PREP AREA

WEEDING AND PACKING

CORRIDOR

STORAGE - LOGGED GOODS

UNPACKING/ CLEANING GOODS IN

STORAGE - NEW GOODS

LOGGING GOODS IN

FINISHED

(PACKED) GOODS OUT

MATERIAL STORAGE

DIRTY AREA

CLEAN AREA

TO OUTSIDE

CORRIDOR

KEY

Door

Work Table

Laser Cutter

Laser Cutter Computer

Other Equipment

Sink

PREP AREA

WEEDING AND PACKING

CORRIDOR

STORAGE - LOGGED GOODS

UNPACKING/ CLEANING GOODS IN

STORAGE - NEW GOODS

LOGGING GOODS IN

FINISHED

(PACKED) GOODS OUT

MATERIAL STORAGE

DIRTY AREA

CLEAN AREA

Operator

## b. Personal Protective Equipment (PPE)

The intent of PPE in this context is to prevent virus from assembly staff contaminating the clips in production. This is important, since asymptomatic individuals can spread the virus through touch and respiration.

The following are to be worn while handling all parts:

- Disposable gloves - replace if removed
- Face masks - paper or fabric masks should be sufficient for this risk. Vented masks should have the valve sealed closed so exhaling is also filtered

# Equipment & Materials

## c. Equipment

- Laser cutters
- Cutting board
- Scalpel
- Scissors
- T7 screwdriver
- Steel weights x 4

## d. BoM Materials

- Custom Cote 0.457mm thick, A2 card
- Clean PE bag 300mm x 400mm
- 2 labels: producer and batch details Avery L4731

## e. Packaging BoM materials

- Bin bags
- 3” packing tape, Brown
- Labels 99mm x 67.5mm for postponed use-after date

## f. Consumables in production

- Permanent Pens labels for labelling
- Surgical masks, disposable or washable - sufficient for 1 mask per Technician per shift
- Disposable latex-free gloves - sufficient for 3 pairs per Technician per shift
- Cleaning cloths for all work surfaces
- Broom to remove production waste
- Mop & bucket

# Preparation of work areas and incoming goods

## 7.1 Cleaning work surfaces and equipment

Work surfaces and equipment must be cleaned before each work session using routine cleaning and disinfection procedures (e.g., use cleaners and water to pre-clean surfaces then apply an EPA-registered, hospital-grade disinfectant). https://www.epa.gov/pesticide-registration/list-n-disinfectants-use-against-sars-cov-2

The process for cleaning the space is as follows:

1. Place cleaning materials on ‘Dirty Goods In’ work table
2. Enter ‘Hygeine and PPE’ area via the marked out gangway only
3. Wash hands for 20 seconds, put on PPE in following order:
  a. Overalls
  b. Surgical Mask
  c. Surgical gloves
4. Clean all work surfaces first with regular cleaning agents, followed by disinfectant
5. Clean all tools with appropriate cleaning wipes, then set them out in correct location as indication by the Production Layout Diagram
6. Return to the ‘Prep Area’ and:
  a. Remove gloves, place in bin
  b. Remove surgical mask, place in bin (if disposable type)
  c. Remove overalls

The area should be cleaned at the start of each work day, or if there is reason to believe the cleanliness of the space may have been compromised (e.g. entry of personnel not wearing correct PPE).

## 7.2 Goods receiving

Incoming goods should be logged and stored, but not completely unpackaged, in the “Incoming Goods” area.

Since viruses may remain viable for several days on surfaces, there is a risk that materials being brought into MakeSpace have been contaminated during distribution. Therefore, outer layers of packaging should be removed wherever possible before bringing materials into the production area.

If the product has not come in appropriate packaging, then it should be cleaned using a clean cloth and appropriate EPA approved disinfectant solution. Cardboard should preferably be left 24hours for virus contamination to become non-viable, rather than cleaning.

Ensure that ‘clean’ goods are placed immediately onto a ‘clean’ table in the ‘Production Area’.

The receipt of goods is traced by the batch history Gsheet, which records the date stamp, operator identification and assigns a unique transaction serial number to the activity.

# 7. Manufacturing process steps

The overall process is as in the diagram below.

A Batch Record is made electronically as work flows, and is mirrored by the packing labels. Traceability will allow us to decide what action to take in the event of an individual displaying symptoms shortly after assembly.

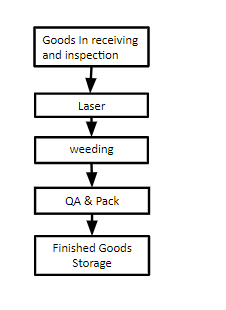
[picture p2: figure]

Material should flow around the workspace as follows:

TO OUTSIDE

CORRIDOR

KEY

Door

Work Table

Laser Cutter

Laser Cutter Computer

Other Equipment

Sink

PREP AREA

WEEDING AND PACKING

CORRIDOR

STORAGE - LOGGED GOODS

UNPACKING/ CLEANING GOODS IN

STORAGE - NEW GOODS

LOGGING GOODS IN

FINISHED

(PACKED) GOODS OUT

MATERIAL STORAGE

DIRTY AREA

CLEAN AREA

# Production Stages

## 7.1 Laser Cutting

In the production tracking software, take out a new lot number. Write this number onto the bag label with your initials, the date and the design designator. Place the label on the bag.

1. Place two sheets of card in the laser cutter, aligned with the alignment jig, and weigh down the corners with steel blocks
2. Laser cut card using cut file XXXA for design A or XXXB for design B
3. Remove sheets using a spare card sheet as a tray and place on weeding table

l

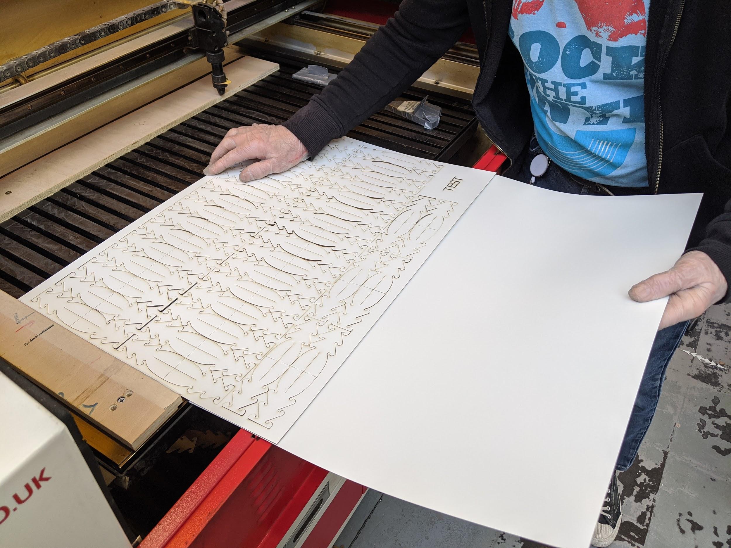
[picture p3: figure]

Laser cutter clearing using a spare sheet as a tray

## 7.2 Post Processing and QA

4. If weeder or QC worker different to cutter operator, record initials on appropriate bag label
5. Separate all clips from skeletal waste by lifting and shaking trim.
6. If still attached use scissors or scalpel to cut free (use cutting board for this).
7. Clear waste from all holes
8. Check clips for non conformance:
  a. Reject clips with deep scratches or marks on the card.
  b. Reject clips with excessive burn marks or staining (max 5mm acceptable).
  c. Reject clips with tears or missing features
  d. Reject clips that have touched the laser waste try, floor or other ‘dirty’ surface
  e. All holes to be clear.
9. Note number of sheets used for inclusion on label.

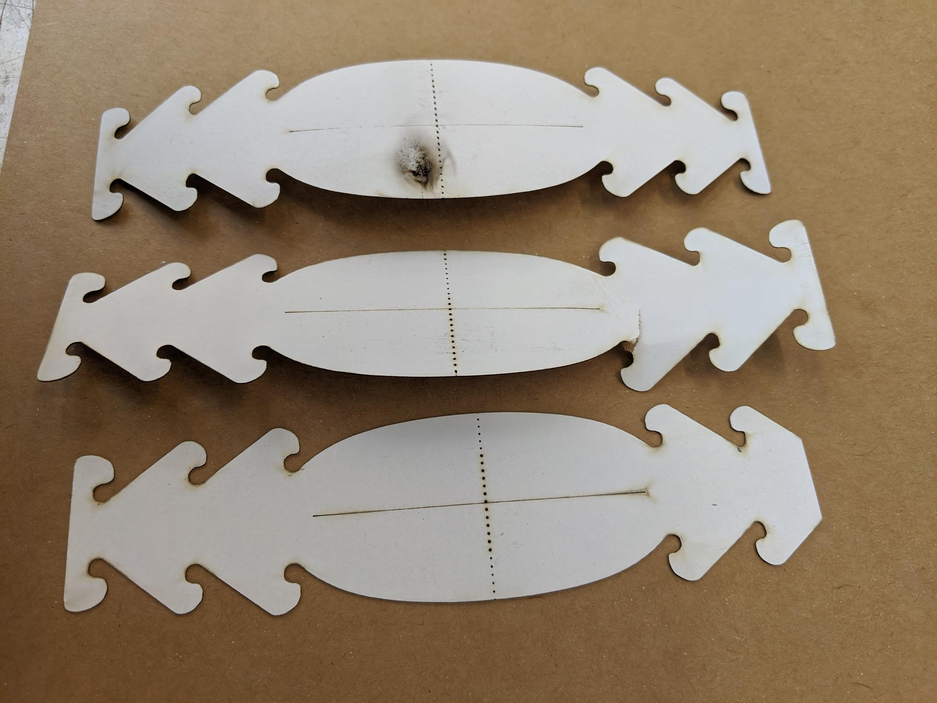
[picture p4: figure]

Example rejection faults on design A

## 7.3 Packing

1. On the bag label, record the number of sheets worth of clips to be bagged (up to a maximum of 8)
2. Place clips in plastic bag, close bag

8 Labelling

The bagged clips are labelled directly with three labels, one to identify the producer, one to record its batch and one to provide instructions for use. They are:

Makespace Labels

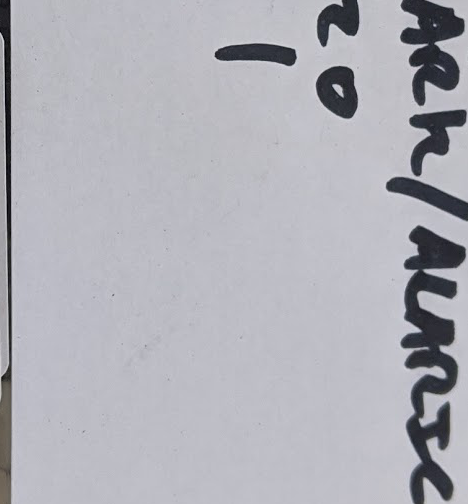
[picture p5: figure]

BagLabels.pdf

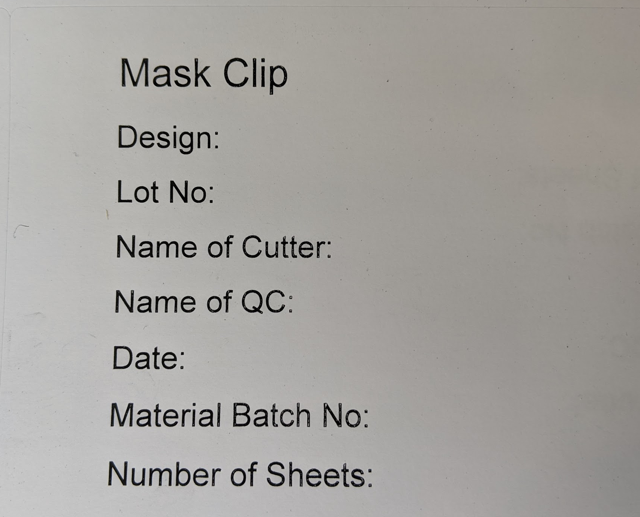
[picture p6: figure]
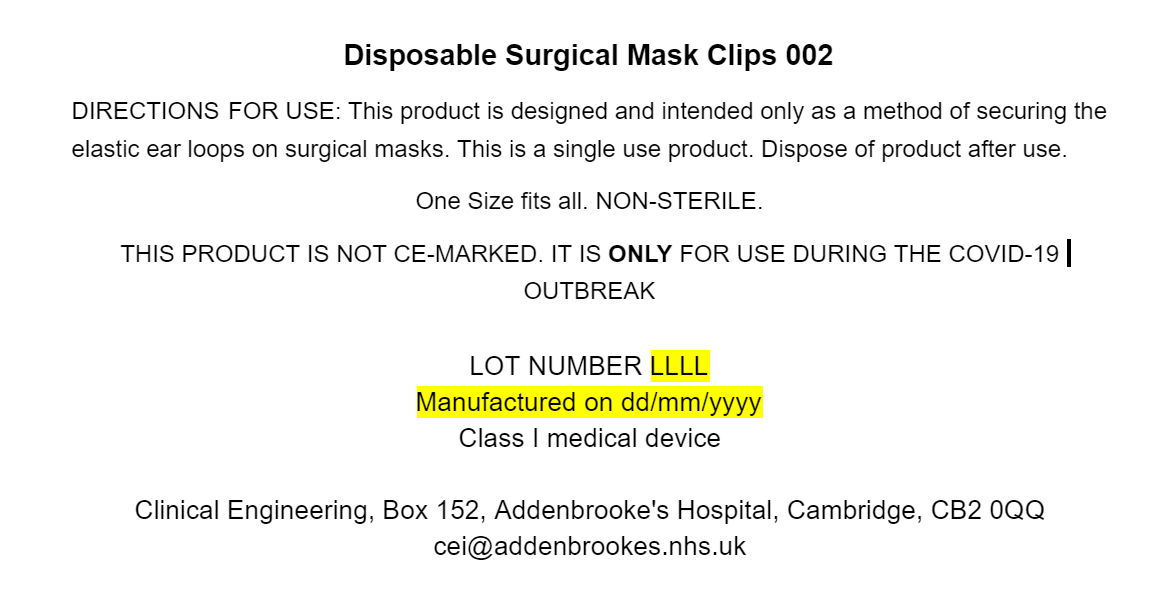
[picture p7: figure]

Manufacturer’s Instructions and Information (Google Doc)

# 9. Supporting Documents

- TBD

# 10. Change History

Version | Changes since previous version | Date / approver
1 | Not applicable, first issue | 22 April 2020 / Abi Bush

Monitoring compliance with and the effectiveness of this document

This process forms part of a quality system accredited to International Standard EN ISO 9001:2015, EN ISO 13485:2016 and BS 70000:2017. The effectiveness of the process will be monitored in accordance with the methods given in the Quality Manual (CE-QS-QAM-4).

Equality and diversity statement

This document complies with the Cambridge University Hospitals NHS Foundation Trust service equality and diversity statement.

Disclaimer

It is your responsibility to check against the electronic library that this printed out copy is the most recent issue of this document.

Document management

Approval:
MDAG approval:
Owning department: | Clinical Engineering Innovation
Author(s): | Mark Mellors
Pharmacist: | n/a
File name: | Manufacturing SOP
Supersedes: | n/a
Version number: | 1.0 | Review date: | n/a
Local reference: | | Document ID:

Page of Surgical Mask Clip SOP v1

Clinical Engineering Innovation Medical Physics and Clinical Engineering

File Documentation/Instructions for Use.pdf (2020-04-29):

# Instructions for Use 22/04/2020

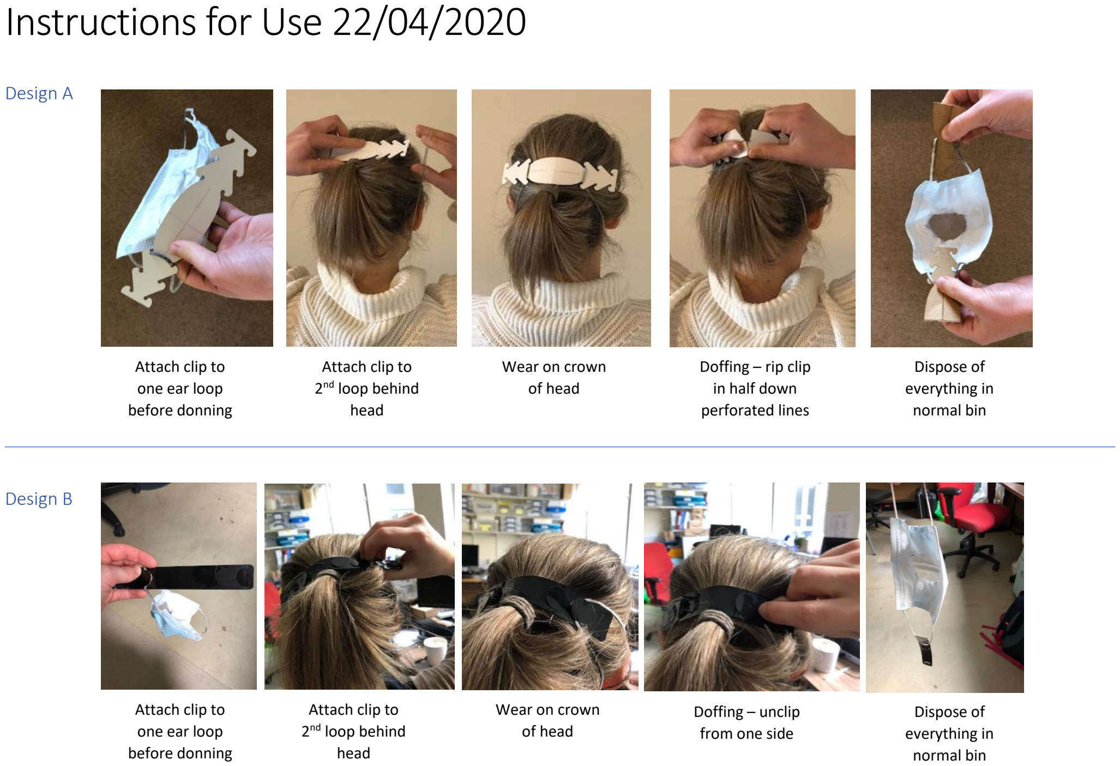
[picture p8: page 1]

### Design A

### Design B

Attach clip to
one ear loop
before donning

Attach clip to
2

nd loop behind
head

Wear on crown
of head

Doffing – rip clip
in half down
perforated lines

Dispose of
everything in
normal bin

Attach clip to
one ear loop
before donning

Attach clip to
2

nd loop behind
head

Wear on crown
of head

Doffing – unclip
from one side

Dispose of
everything in
normal bin
